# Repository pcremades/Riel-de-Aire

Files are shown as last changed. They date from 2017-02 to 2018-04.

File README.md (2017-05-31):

# Riel de Aire
El riel de aire es un equipo diseñado para realizar experimentos de cinemática, dinámica y tabajo y energía. Los carros se desplazan sobre el riel con mínimo rozamiento. El equipo incluye un sistema de adquisición de datos que registra la velocidad de los carros.

# Air Track
The air track is a piece of equipment useful for kinematics, dynamics and energy conservation experiments. The carts move over the air track experiencing minimum friction. This equipment includes a data acquisition system to register the carts speed.

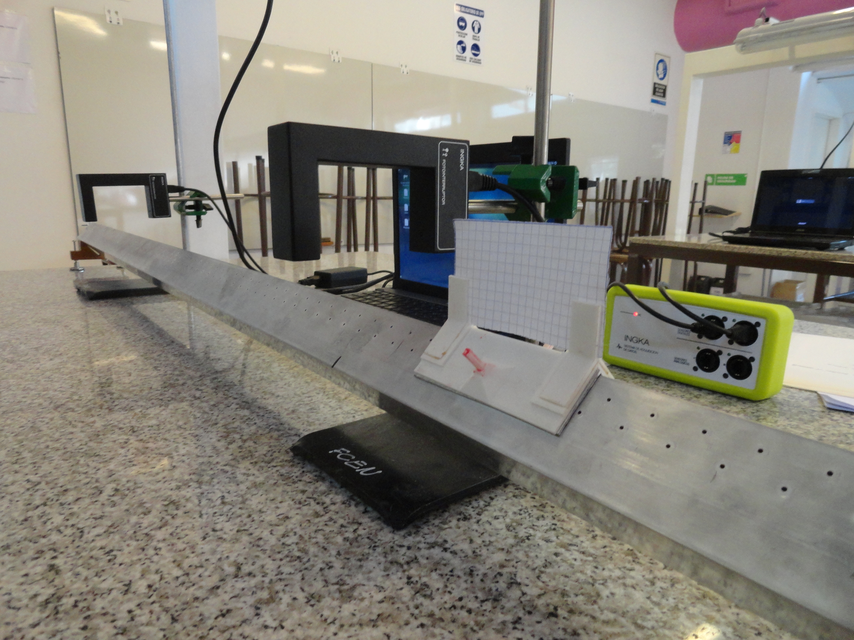
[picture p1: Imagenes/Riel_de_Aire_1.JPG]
Riel de Aire con carro y sistema de adquisición de datos


<br />Esta obra está bajo una <a rel="license" href="http://creativecommons.org/licenses/by-nc/4.0/">Licencia Creative Commons Atribución-NoComercial 4.0 Internacional</a>.

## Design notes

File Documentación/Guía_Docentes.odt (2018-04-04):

# Riel de Aire: guía para docentes

## Materiales

- Riel de aire
- Soplador
- Carro para riel de aire
- Hilo
- Porta-pesas
- Fotocompuerta
- Sistema de adquisición de datos
- PC (opcional)

## Armado

Coloque el riel de aire sobre los soportes de manera tal que el extremo que tiene la polea quede fuera de la mesa.

Inserte la boquilla del soplador en el agujero que se encuentra en el otro extremo del riel de aire.

Coloque una fotocompuerta sobre el riel de aire cerca del extremo del riel de aire que tiene la polea. Conecte la fotocompuerta al sistema de adquisición de datos (y éste a la PC, opcionalmente).

Coloque un carro sobre el riel de aire, encienda el soplador y verifique que el flujo de aire sea suficiente para que el carro se desplace sin rozamiento. El flujo de aire no debe ser excesivo puesto que eso haría que el carro vibre, perdiendo energía cuando está en movimiento.

Coloque un papel rectangular en las pinzas superiores del carro. El mismo actuará de bandera, bloqueando el haz de la fotocompuerta cuando el carro pase por debajo de ella.

Nivele el riel de aire mediante las patas regulables de manera tal que el carro se mantenga quieto en cualquier punto del recorrido cuando sobre éste no actúa ninguna fuerza externa.

Ate un hilo al carro en un extremo y al porta-pesas en el otro extremo.

## Desarrollo

Dibuje para los estudiantes un esquema del sistema a analizar como el que se muestra en la figura 1.

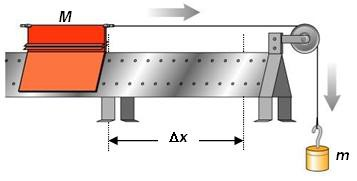
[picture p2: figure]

Fig. 1. Esquema del sistema bajo estudio.

Pida a los estudiantes que encuentren una expresión para la velocidad final del carro (masa M) cuando el contrapeso (masa m) ha caído una altura h. Podrán hacer un análisis dinámico o plantear conservación de la energía mecánica. En el caso de hacer el análisis mediante consideraciones dinámicas, pida a los estudiantes que realicen el diagrama de cuerpo libre de las dos masas. La expresión para la velocidad final está dada por la ecuación 1.

v_f = sqrt{ {2.m.g . h} over {m + M} }
(1)

Luego deberán medir las masas y la altura h para calcular la velocidad final del carro. Además deberán calcular el intervalo de confianza de la velocidad final teórica mediante propagación de errores (ecuación 2):

%DELTA v_f = sqrt{ sum { left ( {partial v_f} over {partial x_i} right )^2 . %DELTA x_i^2 } } = sqrt{ left ( {partial v_f} over {partial m} . %DELTA m right)^2 +
left ( {partial v_f} over {partial M} . %DELTA M right)^2 +
left ( {partial v_f} over {partial h} . %DELTA h right)^2}
(2)

donde los errores estarán dados por los instrumentos utilizados para determinar m, M y h.

Una vez establecido el intervalo de confianza de la estimación de vf, deberán hacer el experimento y hallar el valor experimental de la velocidad final. Deberán realizar varias repeticiones del experimento y encontrar el valor medio y la desviación estándar y comparar los intervalos de confianza teórico y experimental y concluir.

## Sugerencias

Para limitar el recorrido de la masa m, puede atarse un segundo hilo corto al portapesas y el otro extremo al tornillo de la polea, de modo que la masa m se detenga cuando el hilo está completamente extendido. A partir de ahí, la masa M continuará con velocidad constante. De ese modo se consigue que el experimento sea repetible, siempre que el carro se lance desde la misma posición inicial. La fotocompuerta podrá ponerse en cualquier punto del recorrido que se encuentre más allá del punto en el que la masa m ha terminado de caer.

Para medir la altura h, se recomienda medir el desplazamiento del carro sobre el riel de aire entre el punto de partida y el punto en el que el hilo que limita a la masa m está completamente extendido.

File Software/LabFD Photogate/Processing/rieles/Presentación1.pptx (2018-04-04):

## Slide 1

A

Largo de
Bandera (m)

Tiempo(s)

Velocidad(m/s)

B

Tiempo(s)

Velocidad(m/s)

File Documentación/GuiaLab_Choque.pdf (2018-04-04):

### Laboratorio 4

### Trabajo y Energía y Colisiones en 1 Dimensión

Objetivos
- Observar la conservación de la Energía Mecánica en un sistema de fricción despreciable.
- Comprobar la conservación del momento lineal en un choque elástico.
- Comprobar la conservación de la energía cinética en un choque elástico.
- Comprobar la conservación del momento lineal en un choque plástico.
- Hipotetizar sobre qué ocurre con la energía cinética en un choque plástico.

Materiales y métodos
El equipo utilizado consiste en un riel de aire sobre el que los carros pueden desplazarse con fricción despreciable (Figura 1). El equipo cuenta con un sistema de adquisición de datos que permite registrar la velocidad de los carros en cualquier punto del recorrido.
Sobre el riel se colocará un carro de masa M1, que es acelerado por una masa m que cuelga conectada al mismo por medio de un hilo que pasa por una polea de masa despreciable. La masa m se deja caer una altura h fija, que por ser el hilo inextensible coincide con la distancia Δx que se desplaza el carro M1. Cuando la masa M1 ha alcanzado su velocidad final chocará con la masa M2. Se registrarán las velocidades iniciales y finales de los carros, antes y después del choque.

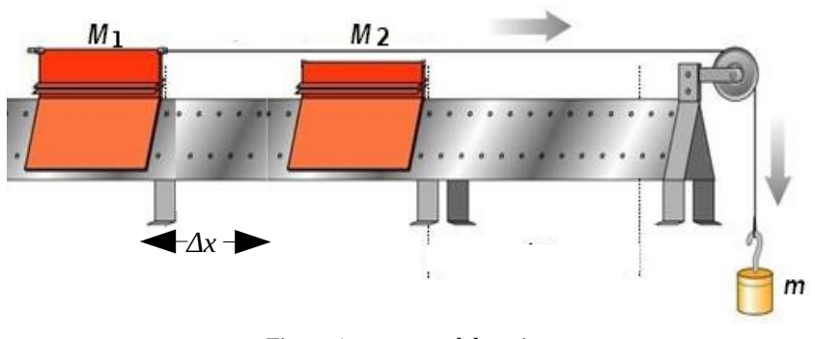
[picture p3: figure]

Figura 1: esquema del equipo.

Descripción de la experiencia
Experiencia 1
1. Utilizando conceptos de Trabajo y Energía, encontrar una expresión para la velocidad final que alcanza el carro M1, en función de los parámetros del sistema.
2. Determinar el intervalo de confianza de la velocidad predicha.
3. Producir choque elástico entre ambos carros, registrando las velocidades iniciales y finales de los carros. Repetir la experiencia varias veces.
4. Determinar la cantidad de movimiento del sistema antes y después del choque. Analizar los intervalos de confianza de las cantidades y concluir.
5. Determinar la energía cinética del sistema antes y después del choque. Analizar los intervalos de confianza de las cantidades y concluir sobre lo que sucede con la energía cinética en este tipo de choques.

Experiencia 2
1. Modificar el sistema para producir un choque inelástico entre los carros. Debe corroborar que los carros continúen unidos luego de producirse el choque.
2. Determinar la cantidad de movimiento del sistema antes y después del choque. Analizar los intervalos de confianza de las cantidades y concluir.
3. Determinar la energía cinética del sistema antes y después del choque. Analizar los intervalos de confianza de las cantidades y concluir sobre lo que sucede con la energía cinética en este tipo de choques.

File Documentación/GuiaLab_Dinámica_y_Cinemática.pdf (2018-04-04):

### Laboratorio 3

Cinemática y Dinámica.

Objetivos
- Observar movimientos rectilíneos tanto uniformes como uniformemente variados, distinguiendo las causas dinámicas de cada uno.
- Modelar el sistema de dos cuerpos que se presenta en el laboratorio planteando las ecuaciones que rigen su movimiento.
- Encontrar una expresión matemática para la variable que se va a medir que permita estimar su valor e intervalo de confianza.

Materiales y métodos
El equipo utilizado consiste en un riel de aire sobre el que los carros pueden desplazarse con fricción despreciable (Figura 1). El equipo cuenta con un sistema de adquisición de datos que permite registrar la velocidad del carro en cualquier punto del recorrido.
En la primer experiencia se colocará un carro de masa M1 sobre el riel y se le dará distintos valores de velocidad inicial, dejándolo moverse libremente sin la acción de ninguna Fuerza Neta aplicada sobre él. Se observan las características de su movimiento.
En la segunda experiencia, sobre el riel se colocará un carro de masa M1, que puede moverse a velocidad constante o puede ser acelerado con una masa m2 conectada al mismo por medio de un hilo no extensible. La masa m se deja caer una distancia fija h, que es la misma distancia Δx que se desplaza en carro M1.

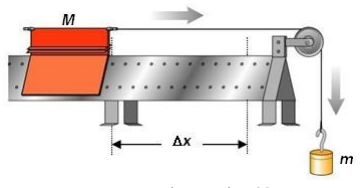
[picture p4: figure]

Figura 1: representación esquemática del equipo.

Experiencia 1
1. Dar distintos valores de velocidad inicial al carro cuando este no se encuentra sometido a la acción de ninguna fuerza neta y verificar que dicha velocidad se mantiene constante en todo el recorrido.

Experiencia 2
1. Se estudia un sistema de dos cuerpos (M1 y m2) conectados por un hilo inextensible de masa despreciable como se muestra en la Fig 1. Encontrar una expresión para la velocidad final que alcanza el carro M1 aplicando los conocimientos de Dinámica. Utilice de Diagramas de Cuerpo Libre para cada objeto y plantee la 2da Ley de Newton para cada objeto.
2. Con la expresión hallada para la velocidad final de M1, prediga su valor y determine su intervalo de confianza.
3. Verifique experimentalmente el valor de la velocidad final. Establezca el intervalo de confianza de la velocidad medida realizando varias repeticiones.
4. Concluya sobre el valor teórico y el valor experimental obtenidos.

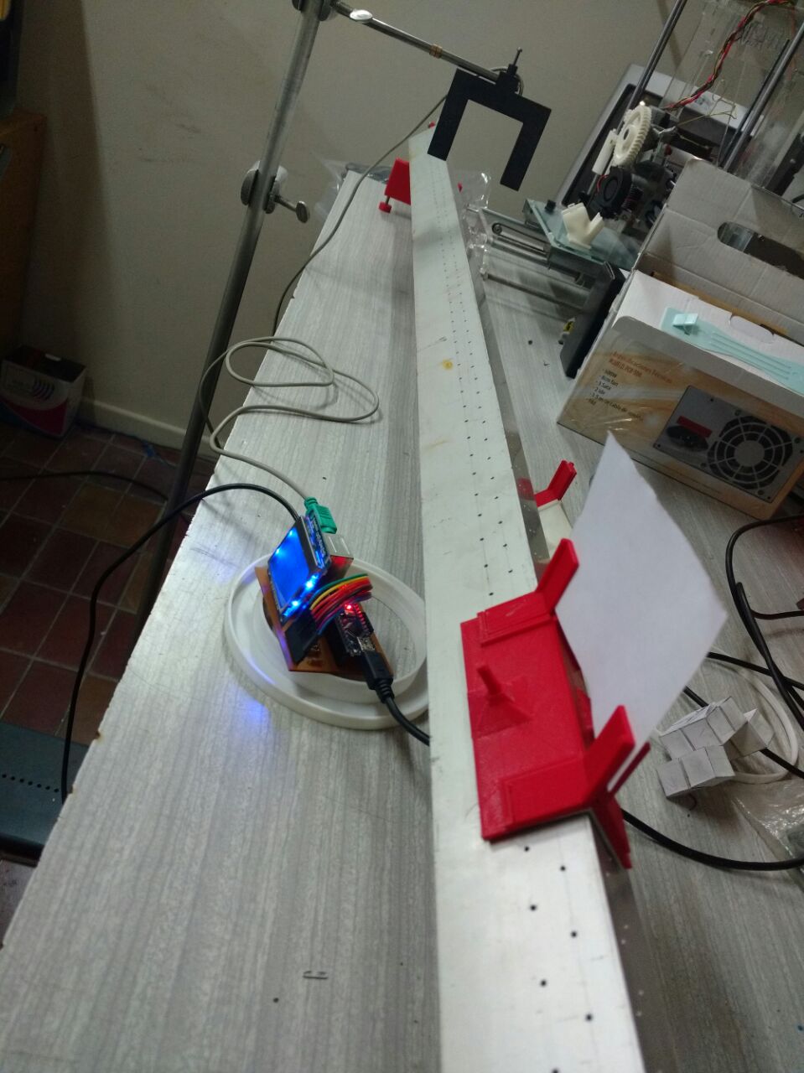
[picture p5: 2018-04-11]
Imagenes/Riel UTN-WA0014.jpg

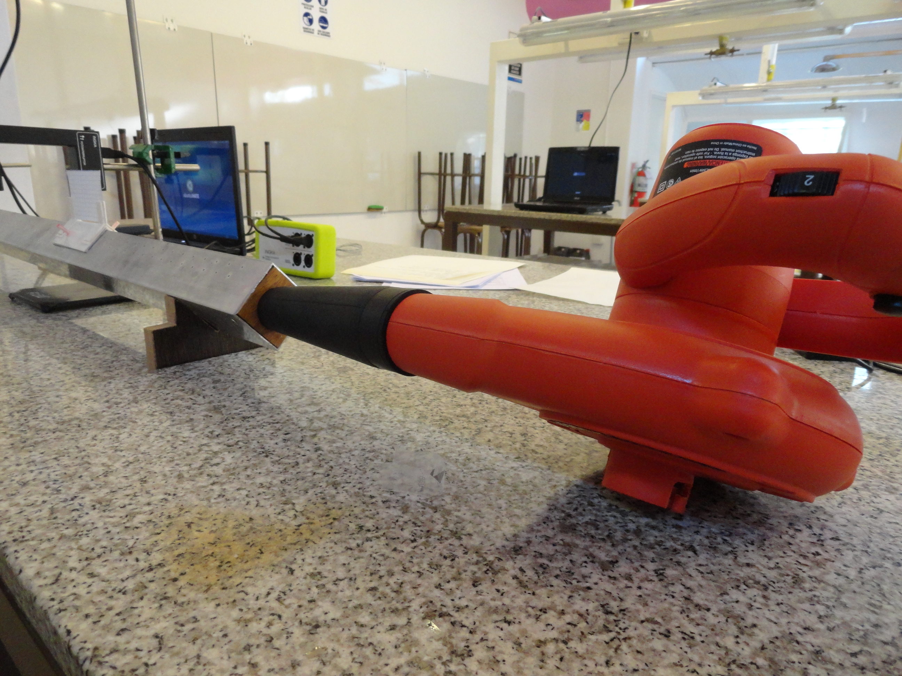
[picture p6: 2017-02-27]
Imagenes/Riel_de_Aire_2.JPG

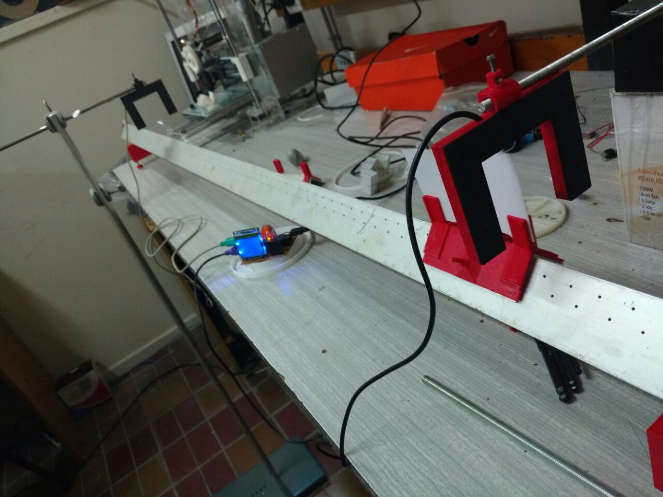
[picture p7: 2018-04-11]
Imagenes/Riel UTN-WA0011.jpg

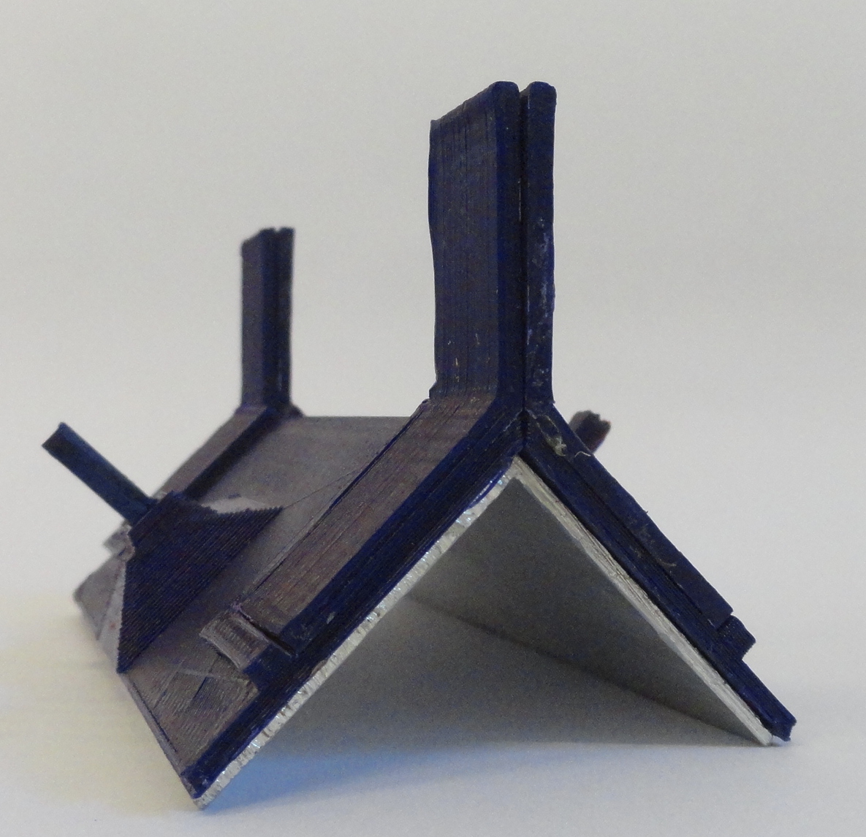
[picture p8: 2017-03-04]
Imagenes/Carro_2.JPG

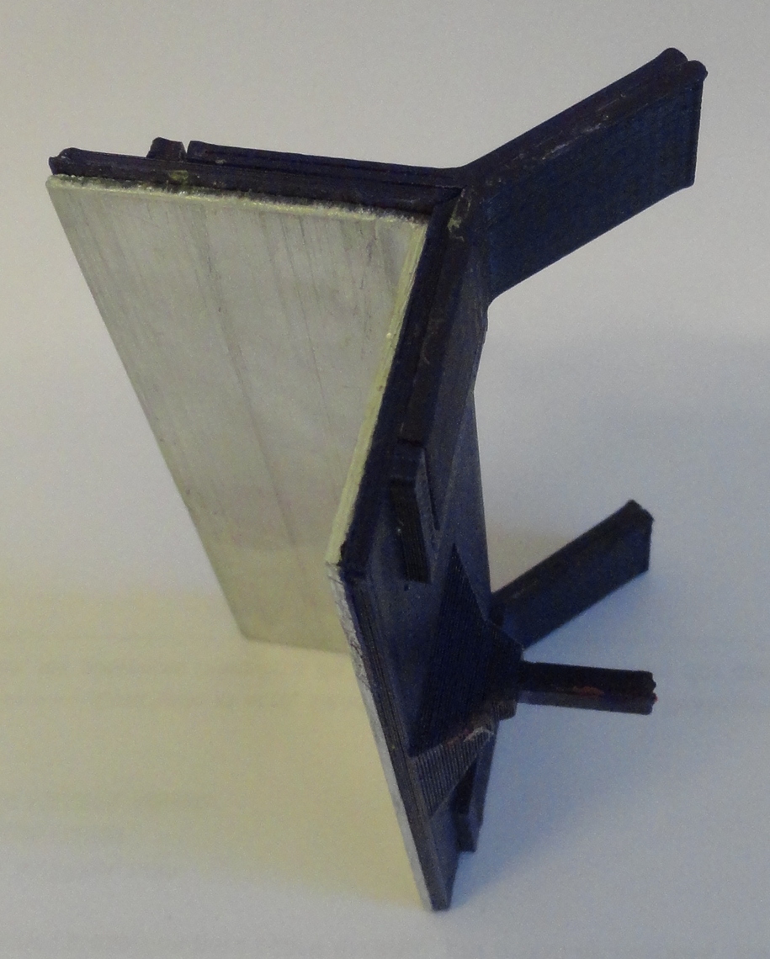
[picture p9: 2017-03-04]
Imagenes/Carro_3.JPG

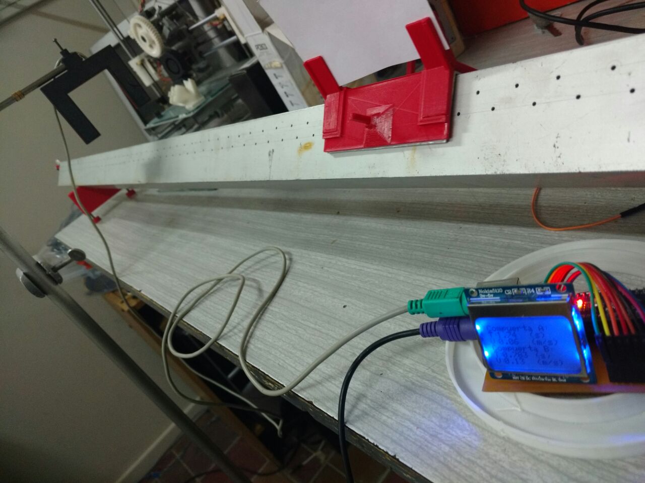
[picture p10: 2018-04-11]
Imagenes/Riel UTN-WA0018.jpg

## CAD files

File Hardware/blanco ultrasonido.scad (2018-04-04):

union(){
rotate([-90,0,0])
cube([40,30,2],center=true);
pest();
mirror([1,0,0])
pest();
}


module pest(){
linear_extrude(15)
polygon([[4.6,1],[4.6,3.5],[2.2,3.5], [2.2,5.2],[6.2,5.2],[6.2,5],[11,1]]);
}

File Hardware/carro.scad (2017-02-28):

// -------- Este módulo fue creado por Fernando Castro 	--------
// -------- on the 10/08/2016 y está disponible  para ser distribuido sin restricciones.

// Elementos que componen el carro

render_part(2);
module render_part(part_to_render) {
	if (part_to_render == 1) pestania();
    if (part_to_render == 2) basecompleta();
    if (part_to_render == 3) vastago();
}

// Dimensiones de la pestaña
ancho_p=15;
largo_p=25;
espesor_p=2;

// Dimensiones de la base del carro
ancho_b=35;
largo_b=100;
espesor_b=2;
    //Dimensiones soporte para pesos
    vastago_b=3.5;
    vastago_h=20;
    base=10;
    altura=10; 

module base(){
difference(){
cube(size=[ancho_b+espesor_b/2,largo_b,espesor_b]);
color("red")
rotate([0,-45,0])
cube(size=[espesor_b+espesor_b/2,largo_b*2+2,espesor_b*2],center=true);
}}

module traba_p()
{union(){
    color("red")
translate([0,ancho_p,espesor_b])
cube(size=[largo_p,espesor_p+1,espesor_p]);
color("red")
translate([largo_p,0,espesor_b])
cube(size=[espesor_p+1,ancho_p+espesor_p+1,espesor_p]);
}}

module soporte(){
color("green")
translate([ancho_b-base,largo_b/2,0])
difference(){
union(){
translate([-vastago_b/2,0,0])
rotate([0,0,45])
cylinder(altura,base,vastago_b,$fn=4);
rotate([0,0,45])
cylinder(altura-vastago_b/2,base*2,vastago_b,$fn=4);
}
translate([-vastago_b/2,0,0])
cube(size=[vastago_b,vastago_b,altura*2],center=true);
translate([base,0,0])
cube(size=[vastago_b*4,base*4,vastago_b],center=true);
}}
module basecompleta(){
union(){
base();
traba_p();
mirror([0,1,0])
translate([0,-largo_b,0])
traba_p();
soporte();
}}

module pestania(){
rotate([90,0,0])
union(){
    cube(size=[largo_p,ancho_p,espesor_p]);
translate([largo_p,0,0])
    rotate([0,-45,0])
cube(size=[largo_p,ancho_p,espesor_p]);
}}
module vastago(){
    rotate([90,0,0])
    cube(size=[vastago_b,vastago_b,vastago_h]);
    }

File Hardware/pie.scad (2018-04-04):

$fn=100;
tuborect=50;
espesor=20;
ancho=2*tuborect*cos(45)+2*15;
alto=50;

Set_Screw_Diameter=5; //[2:10]
//Set Screw Nut Diameter
Set_Screw_Nut_Diameter=9; //[4:20]
//Set Screw Nut Thickness
Set_Screw_Nut_Thickness=4; //[2:10]
Set_Screw_Largo=28; //[2:10]
//-------------------------------
a=Set_Screw_Diameter; //[2:10]
//Set Screw Nut Diameter
b=Set_Screw_Nut_Diameter; //[4:20]
//Set Screw Nut Thickness
c=Set_Screw_Nut_Thickness; //[2:10]
d=Set_Screw_Largo;

pie();
//apoyo_inf();
//apoyo_sup();
module pie(){
difference(){
cube([ancho,espesor,alto],center=true);
translate([0,0,50*cos(45)])
rotate([0,45,0])
cube(50,center=true);

translate([-tuborect*cos(45)-15/2,0,-alto/2-d/8])
cylinder(d,a/2+0.2,a/2+0.2);
translate([-tuborect*cos(45)-15/2,0,-alto/3-c/2])
rotate([-90,0,90])
#nuttrap();

translate([tuborect*cos(45)+15/2,0,-alto/2-d/8])
cylinder(d,a/2+0.2,a/2+0.2);
translate([tuborect*cos(45)+15/2,0,-alto/3-c/2])
rotate([90,0,90])
#nuttrap();}
}
module apoyo_inf(){
difference(){
cylinder(c,b,b,center=true);
hexagon(c,b/2+0.2);
}}
module apoyo_sup(){
difference (){
cylinder(c,b,b,center=true);
translate([0,0,-c])
hexagon(c,b/2+0.2);
cylinder(c,a/2+0.2,a/2+0.2);
}}

module nuttrap(){
translate([0,(c+1)/2,0])rotate([90,0,0])hexagon(c+1,(b+1)/2);
translate([0,0,(b*3)/2])cube([b+1,c+1,b*3],center = true);
}
module hexagon(height,radius) 
{
  linear_extrude(height=height) hexagonf(radius);
}

module hexagonf(radius)
{
  reg_polygon(6,radius);
}
module reg_polygon(sides,radius)
{
  function dia(r) = sqrt(pow(r*2,2)/2);  //sqrt((r*2^2)/2) if only we had an exponention op
  if(sides<2) square([radius,0]);
  if(sides==3) triangle(radius);
  if(sides==4) square([dia(radius),dia(radius)],center=true);
  if(sides>4) circle(r=radius,$fn=sides);
}

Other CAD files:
Hardware/soporte polea.scad
Hardware/UGroovePulley.scad
Hardware/soporte_polea.scad
Hardware/tapa.scad

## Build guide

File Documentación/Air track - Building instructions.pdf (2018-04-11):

Linear air track

This equipment is designed to perform experiments of kinematics, dynamics and mechanical energy conservation, minimizing the effect of friction.

BOM

Count | Metals
1 | Rectangular aluminium tube 2 meters long
1 | MDF 30cm x 30cm (1” thick)
1 | Bearing (aprox 8 mm external diameter)
1 | M3 x 20 mm screw
1 | M3 hex nut
| 3D printed parts
2 | basecompleta (carro.scad)

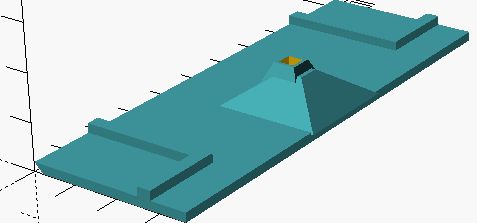
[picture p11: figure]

4 | pestania (carro.scad) | 1
2 | vastago (carro.scad)
1 | polea (UgroovePulley.scad)
1 | soporte (soporte polea.scad)

2 | pie (pie.scad)

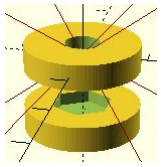
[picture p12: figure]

4 | apoyo inferior y apoyo superior (pie.scad)

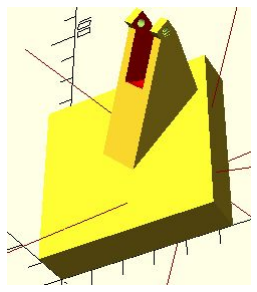
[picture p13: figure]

1 | Tapaypolea (tapa y soporte.scad)

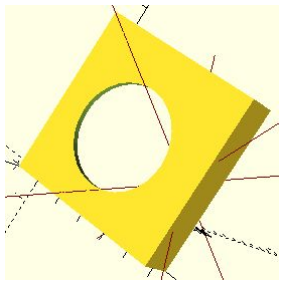
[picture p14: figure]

1 | Tapasoplador (tapa y soporte.scad)
| Tools
1 | cup drill bit 30 mm (it depends on the blower outlet)
1 | Metal drill bit 1 - 1.5 mm

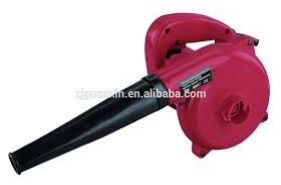
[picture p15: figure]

1 | blower machine

Building instructions

Track

Cut a 10 cm piece of the rectangular aluminum tube that is going to be used to build the carts. On 2 adjacent faces of the aluminum tube draw two lines parallel to the edge all along the tube. The first line should be separated 1 cm from the edge and the second one 2 cm from the edge (Fig. 1).

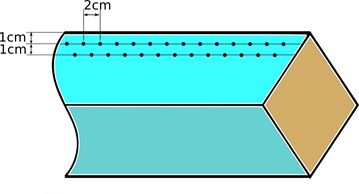
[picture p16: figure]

Fig 1. Tube drilling scheme

Perform holes of 1 - 1.5 mm with the metal drill bit in a way that the holes are separated 2 cm among them. In the second line make sure the holes are displaced 1 cm with respect to those on the upper row.

Track caps

Print the tapaypolea and tapasoplador (tapas.scad) and put each on one side of the track.

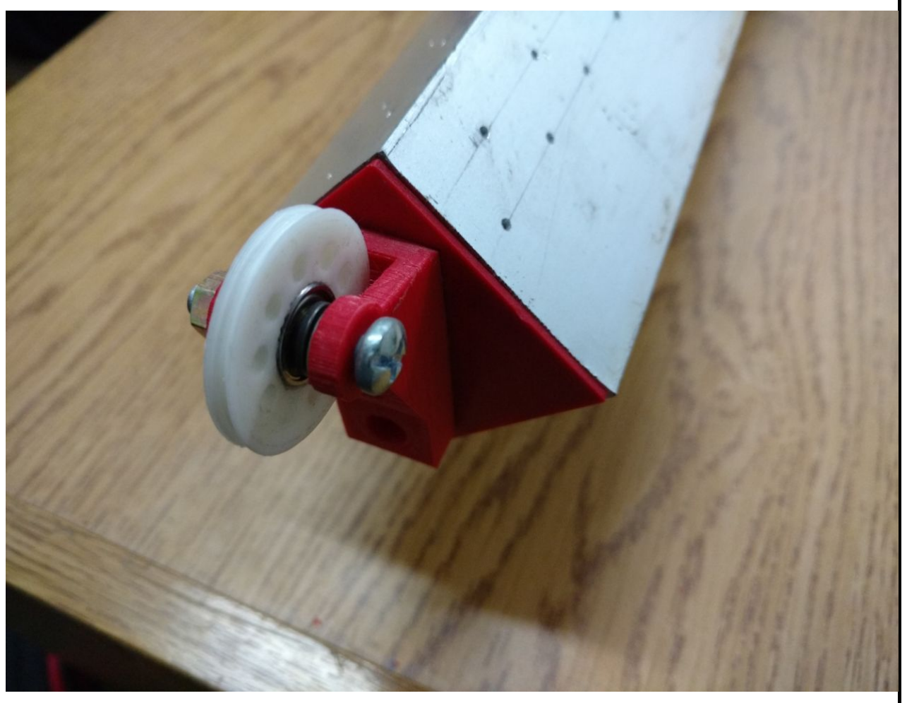
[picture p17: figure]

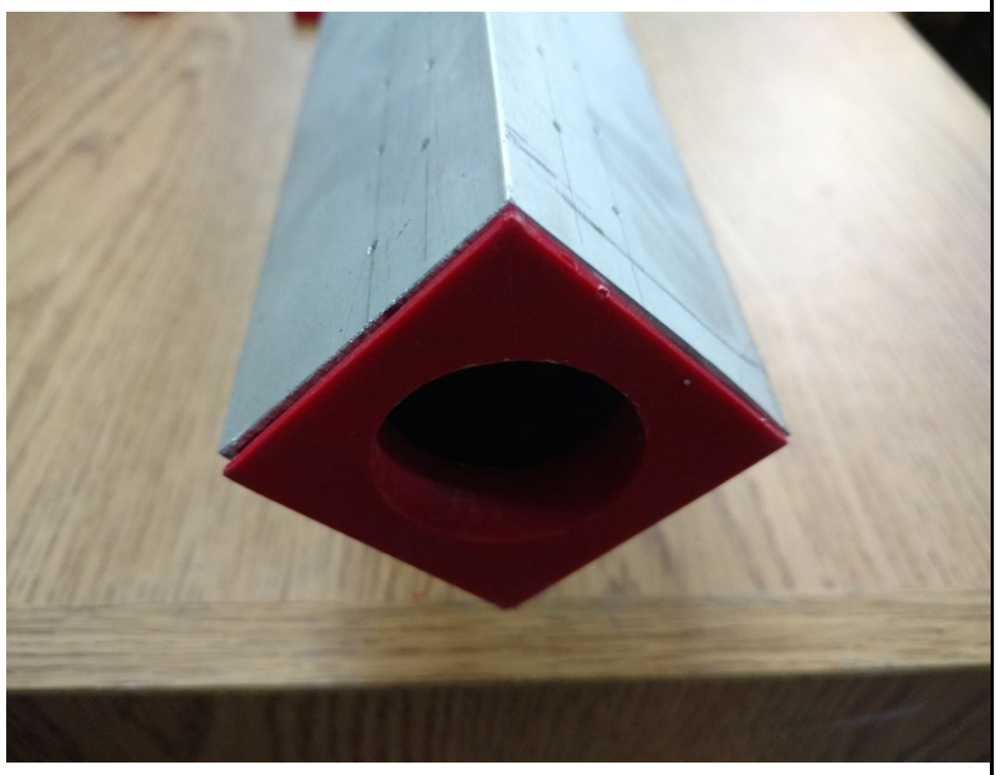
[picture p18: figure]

Fig 2. Blower and pulley cap

Track holder

Print 2 pie (holder) and 4 supports (pie.scad) and with the M5 screws and the nuts make two adjustable legs as in Fig 2.

Fig. 3: track holder scheme.

Carts
In order to build the carts, cut 2 L shape aluminum pieces of 3,5 cm from the 10 cm long piece of aluminium tube (Fig. 4).

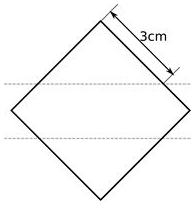
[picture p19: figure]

Fig. 4: cross section of the 10 cm piece of aluminium tube

On top of the L shape pieces glue the 3D printed parts of the cart (3 parts of carro.scad) as in Fig. 5

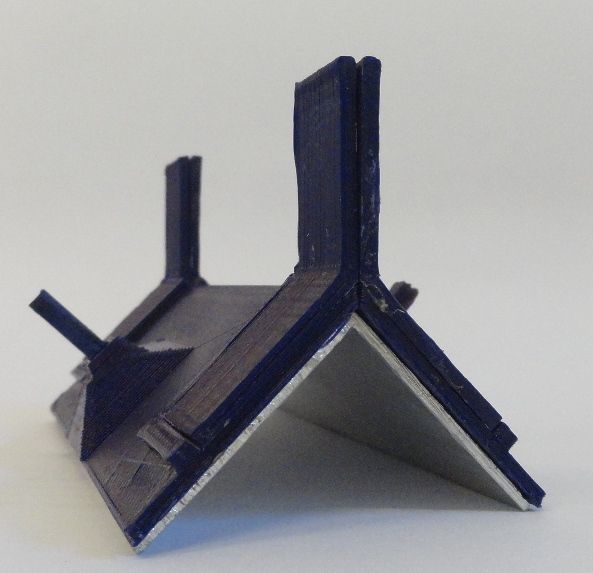
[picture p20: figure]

Figure 5. Cart

Pulley
The pulley (UGroovePulley.scad) has been design to hold an 8 mm diameter ball bearing (can be scavenged from CPU or power supply cooler fan). The ball bearing must fit into the pulley and then it must be placed into the cap with the pulley holder (tapaypolea) with the M3 screw as the axle. Make sure that the pulley is just above the edge of the track (Figure 6).

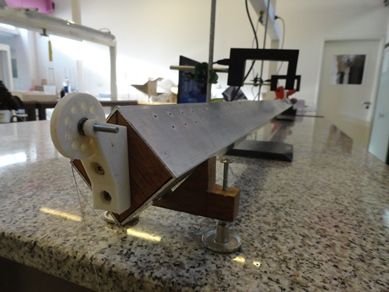
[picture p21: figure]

Figure 6. Pulley cap

Datalogger and photogates
This version of the air track is based on a local proprietary platform (INGKA http://www.ingka.com.ar/) to register the cart speed. This system can be replaced with an open source datalogger and photogate as the one of LabFD (https://github.com/nanocastro/Fotocompuerta-LabFD)

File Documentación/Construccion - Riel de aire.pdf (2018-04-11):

Riel de aire

Este equipo está diseñado para realizar experimentos de cinemática, dinámica y conservación de la energía mecánica, reduciendo al mínimo el efecto del rozamiento.

Lista de materiales

Count | Partes metálicas | Comentario/Imagen
1 | Caño de aluminio de sección cuadrada (5cm x 5 cm) de 2m de longitud aproximadamente
1 | MDF 30cm x 30cm (1” thick)
1 | Rulemán de 8mm de diámetro externo
1 | Tornillo M3 x 20 mm
1 | Tuerca M3
4 | Tornillos M5 x 20mm de cabeza hexagonal
4 | Tuercas M3
| 3D printed parts
2 | basecompleta (carro.scad)


4 | pestania (carro.scad) | 1
2 | vastago (carro.scad)
1 | polea (UgroovePulley.scad)
1 | soporte (soporte polea.scad)

2 | pie (pie.scad)

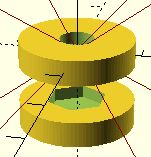
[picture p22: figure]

4 | apoyo inferior y apoyo superior (pie.scad)


1 | Tapaypolea (tapa y soporte.scad)

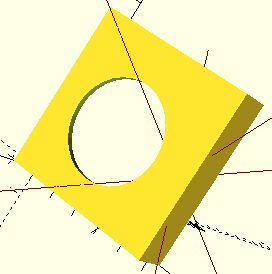
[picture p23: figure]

1 | Tapasoplador (tapa y soporte.scad)
| Tools
1 | cup drill bit 30 mm (it depends on the blower outlet)
1 | Metal drill bit 1 - 1.5 mm


1 | blower machine

Construcción

Riel

Cortar un tramo de 10cm aproximadamente del caño, que luego se utilizará para construir los carros.

Sobre 2 caras adyacentes del caño de aluminio marcar 2 líneas paralelas a la aristas, de un extremo al otro del caño. La primera línea debe estar a 1cm de la arista y la otra, paralela a la primera, a 2cm de la arista (Fig. 1).

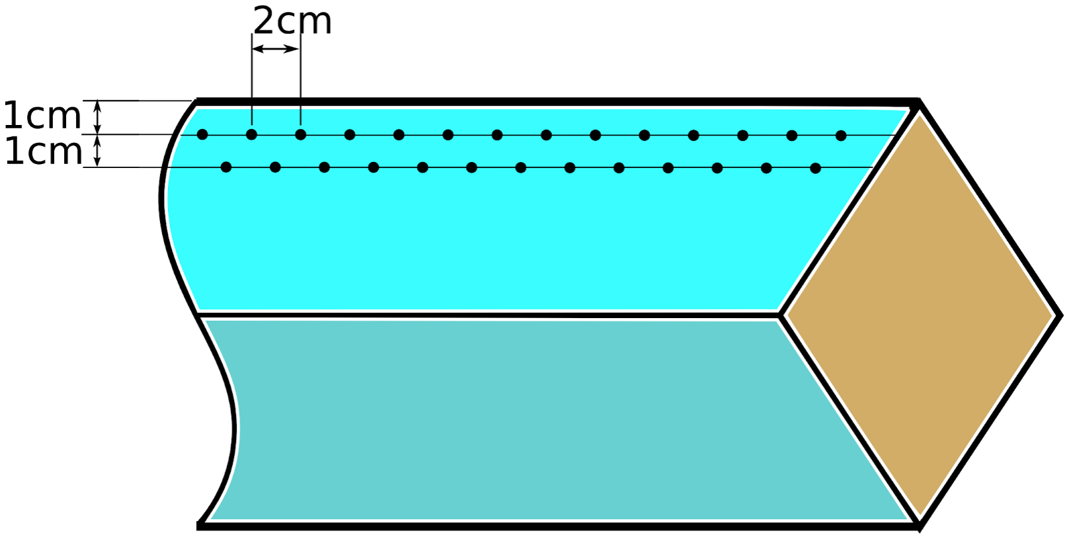
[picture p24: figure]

Fig. 1: esquema del caño con las perforaciones.

Practicar perforaciones de 1mm o 1.5mm sobre las líneas, de manera que los agujeros tengan una separación de 2cm entre sí. En la segunda línea, procurar que los agujeros estén desplazados 1cm respecto la los de la fila anterior.

Tapas del riel

Imprimir las piezas tapaypolea y tapasoplador (tapas.scad) y colocar cada una en los dos extremos del caño rectangular

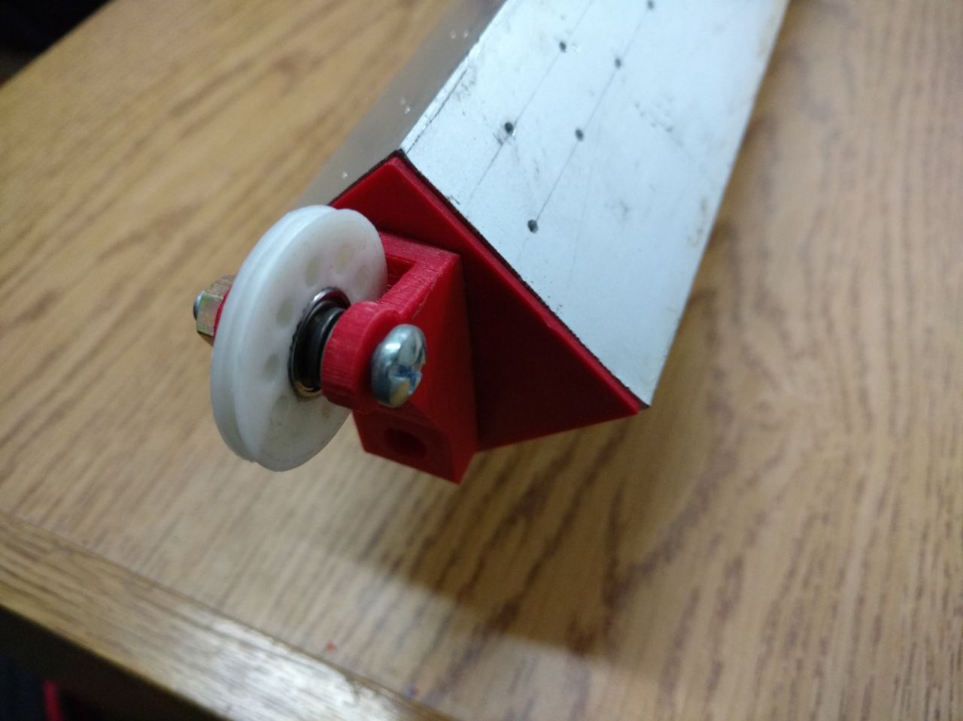
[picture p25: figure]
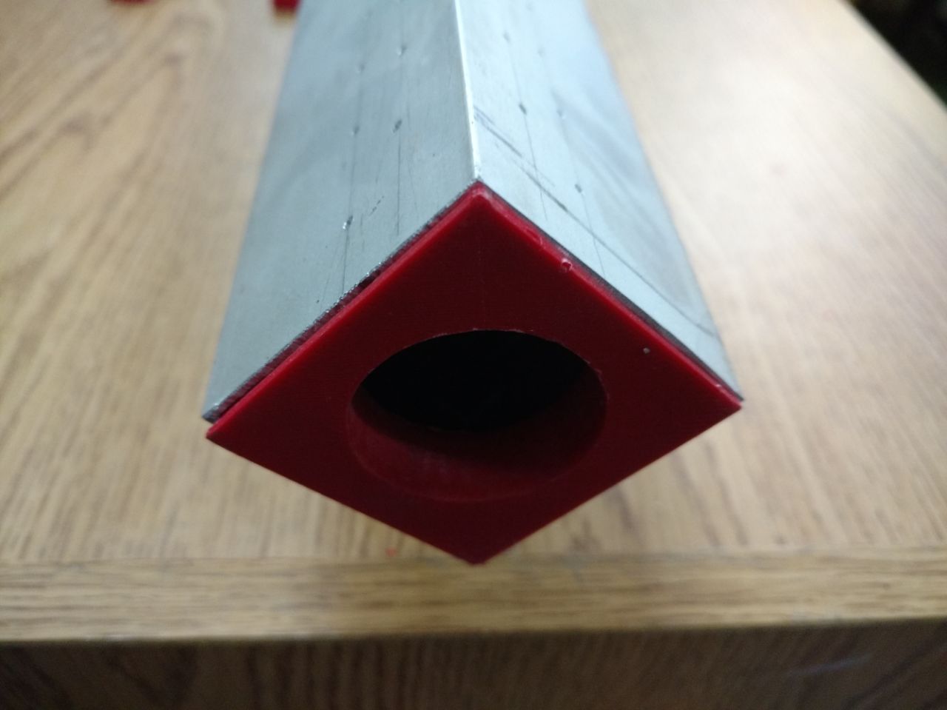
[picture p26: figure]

Pies del riel

Imprimir 2 pies y 4 apoyos (pie.scad) y armar con los tornillos y las tuercas M5 las patas regulables tal como se muestra en la Figura 2.

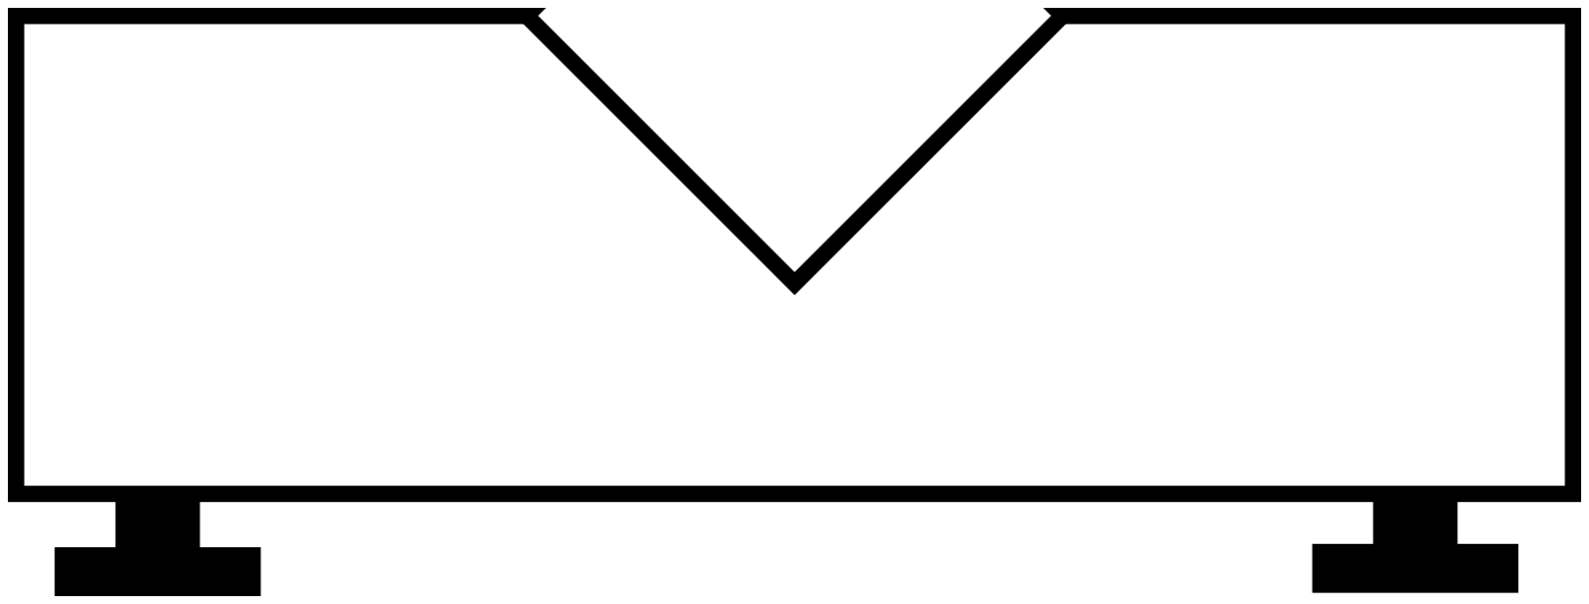
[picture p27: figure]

Fig. 2: esquema de los soportes del riel.

Carros

Para los carros, tomar la sección restante del caño de aluminio (10cm de longitud) y cortar 2 perfiles L de 3cm de lado (Fig. 3).

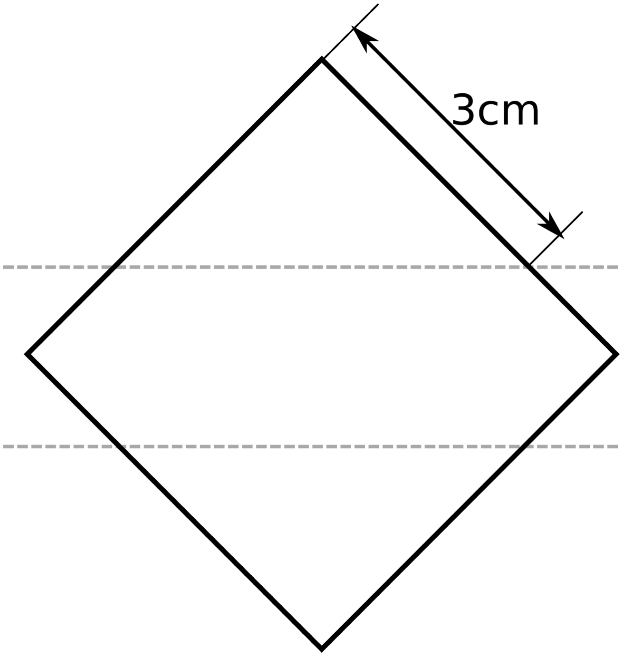
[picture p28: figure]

Fig. 3: sección transversal del caño. Cortes para obtener los 2 perfiles L que conforman los carros.

Sobre los perfiles de aluminio, pegar con cemento de contacto las piezas plásticas que conforman los carritos (las tres piezas de carro.scad).

Polea

Finalmente, la polea (UGroovePulley.scad) está diseñada para utilizar un rulemán de 8mm de diámetro (como el que se encuentra en los ventiladores de los procesadores de PC o de fuentes de PC). El rulemán se coloca en la polea y luego el conjunto en la tapa del riel tapaysoporte mediante un tornillo de 3mm a modo de eje. Procurar que la rueda quede ligeramente por encima de la arista del caño.

Sistema de adquisición de datos

El equipo cuenta con un sistema que registra la velocidad de los carros. El sistema está basado en una plataforma comercial Argentina llamada INGKA (http://www.ingka.com.ar/). Es una plataforma propietaria, pero se puede reemplazar fácilmente por esta fotocompuerta (https://github.com/nanocastro/Fotocompuerta-LabFD) . El sistema de adquisición permite conectar 2 fotocompuertas. Las mismas registran el tiempo que tarda el carro en pasar por el sensor y calculan la velocidad media. Para esto, es necesario montar sobre los carros una bandera de longitud conocida.

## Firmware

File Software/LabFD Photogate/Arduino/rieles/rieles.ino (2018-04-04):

#include <SPI.h>
#include <Adafruit_GFX.h>
#include <Adafruit_PCD8544.h>

Adafruit_PCD8544 display = Adafruit_PCD8544(8, 7, 6, 5, 4);

int IRD1=2, IRD2 = 3, IRE1=12, IRE2=11;
float evento1=0, evento2 =0, duracion=0;
boolean estadoc1, estadoc2, estadoc01=0, estadoc02=0; 
String msj;
int m=0,n=0,c=0;

void setup() {
  
  display.begin();
  display.setContrast(50);
  display.display(); 
  Serial.begin(115200); 
  pinMode(IRD1, INPUT_PULLUP);
  pinMode(IRD2, INPUT_PULLUP);
  pinMode(IRE2, OUTPUT);
  pinMode(IRE1, OUTPUT); 
  pinMode(13, OUTPUT); 
  digitalWrite(IRE1, HIGH); 
  digitalWrite(IRE2, HIGH);
  delay(1000);
  display.clearDisplay();
  display.display();
  display.setCursor(0,0);
  display.println("Compuerta A:");
  display.setCursor(0,8);
  display.println("T:      (s)");
  display.setCursor(0,16);
  display.println("V:      (m/s)");
  display.setCursor(0,24);
  display.println("Compuerta B:");
    display.setCursor(0,32);
  display.println("T:      (s)");
  display.setCursor(0,40);
  display.println("V:      (m/s)");
  display.display();
}

void loop() {
  estadoc1=digitalRead (IRD1);
  estadoc2=digitalRead (IRD2);
  digitalWrite(13, !estadoc1);
  
      if (estadoc1!=estadoc01)
      {
        if(n==0){
            evento1=millis();
            msj="A";//msj sirve para identificar las puertas al comunicarse con procesing
            Serial.println(msj);
            n++;
            }else if(n==1){
                      evento2=millis();
                      duracion=(evento2-evento1);
                      msj="A";
                      msj.concat(duracion);
                      display.setCursor(10,8);
                      display.setTextColor(BLACK, WHITE);
                      display.println(duracion/1000.000);
                      display.setCursor(10,16);
                      display.println(0.1/(duracion/1000.000));//0.1m largo de la bandera
                      display.display();
                      Serial.println(msj);
                      n=0;
            }
                  
        }
      estadoc01=estadoc1;    
      if (estadoc2!=estadoc02)
      {
        if(m==0){
            evento1=millis();
            msj="B";
            Serial.println(msj);
            m++;
            }else if(m==1){
                      evento2=millis();
                      duracion=evento2-evento1;
                      msj="B";
                      msj.concat(duracion);
                      display.setCursor(10,32);
                      display.setTextColor(BLACK, WHITE);
                      display.println(duracion/1000.000);
                      display.setCursor(10,40);
                      display.println(0.1/(duracion/1000.000));
                      display.display();
                      Serial.println(msj);
                      m=0;
            }
                  
        }
      estadoc02=estadoc2;
}

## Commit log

2017-05-16 Add files via upload
    traduccion de las instrucciones
2017-05-17 Add files via upload
    Versión corregida de las instrucciones en inglés
2018-04-04 Reemplazo con el repositorio que está en Física_1/Riel_Aire
2018-04-04 Agrego cambios del Nano
    [blanco ultrasonido.scad, pie.scad, soporte_polea.scad]
2018-04-05 Agrego app para sensor ultrasónico
2018-04-10 Subo imagen del experimento del riel de aire
2018-04-11 Updated via the Open Science Framework
2018-04-11 agrego diseño tapa y cambio instrucciones construccion
    [tapa.scad]
